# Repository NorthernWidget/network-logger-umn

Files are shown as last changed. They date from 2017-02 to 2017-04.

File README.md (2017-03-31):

Logger
======
This code is heavily based off the Alog library by Northern Widget. When
completed, this implementation will include radio telemetry using the RFM69 chip
for RF communication. This library is currently a work in progress and should
not be expected to work on its own. Expect a working copy in early May.
The new libraries in this repo are the Network.cpp, Network.h, Queue.cpp,
Queue.h, and Packet.h files. In total about 650 lines of code were added.

How to use the Network:

In order to use the network in the Logger Library, the user need only call 2
functions: sendOverNetwork(float data) with a floating point of the data that
they want to send to the coord, and then runNetwork(). runNetwork() is the
heart of the network library. It takes care of keeping up each nodes connection
to the coordinator, and handling any packets it receives or needs to send. A 
more detailed description of the algorithm can be found below, but these two
functions are all the end user NEEDS to get the network rolling.

A more detailed description:

The network algorithm works like so in pseudocode:

runNetwork()
{
	//condition 1 we are the coord listen for data
	if(IamCoord)
	{
		listen for incoming data and upload it to server
	}
	//condition 2 we have a connection to the coord, send data
	else if(IhaveConnectionToCoord)
	{
		send all of my data towards coord
		listen for data to forward to coord
	}
	//condition 3 we do not have connection to the coord
	else
	{
		try to connect to coordinator
	}
}
A few notable points in this algorithm. Originally, we were trying to forward
the data from the furthest leaf nodes to the router nodes first, then forward it
to the coordinator, but there is a nightmare of timing issues and other
complexities. Then we decided to do the opposite:send the data from the closest
nodes to the coordinator first. Therefore in condition 2, all the nodes that
aren't coord will be sending their data over and over again until it finally
reaches the coordinator. Then they will start listening for other nodes that
are using them as a next hop to get to the coord, and forward that data. This
eliminates a lot of the timing issues, and the need for each node to know the
other nodes depending on it.

Contributors to the network enabled ALog: Luke Cesarz, Jeff Worm, David Nickel,
Ying Yang, Bobby Schulz

Data logger library for the Arduino-based ALog (http://northernwidget.com/?page_id=8)

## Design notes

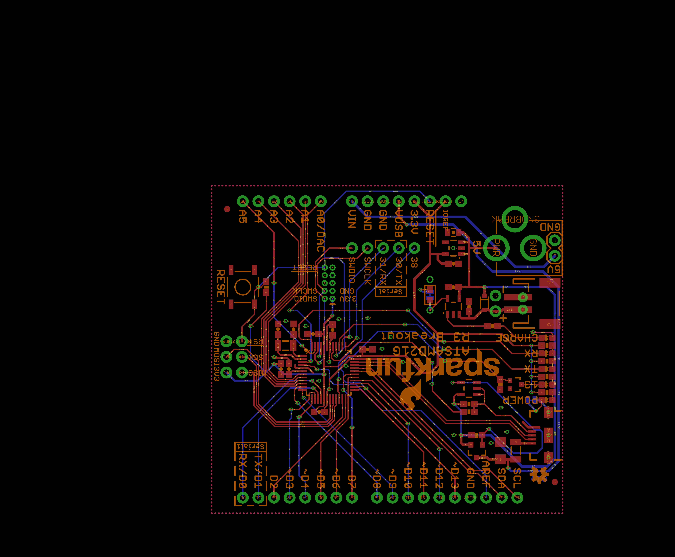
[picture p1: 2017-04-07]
Hardware/Logger v2/SAM21.png

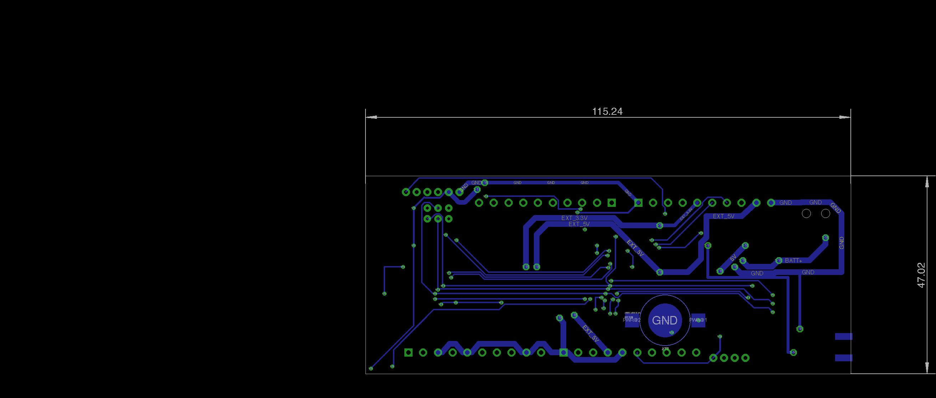
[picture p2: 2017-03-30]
Hardware/Logger v2/Logger_v2_BOTTOM.png

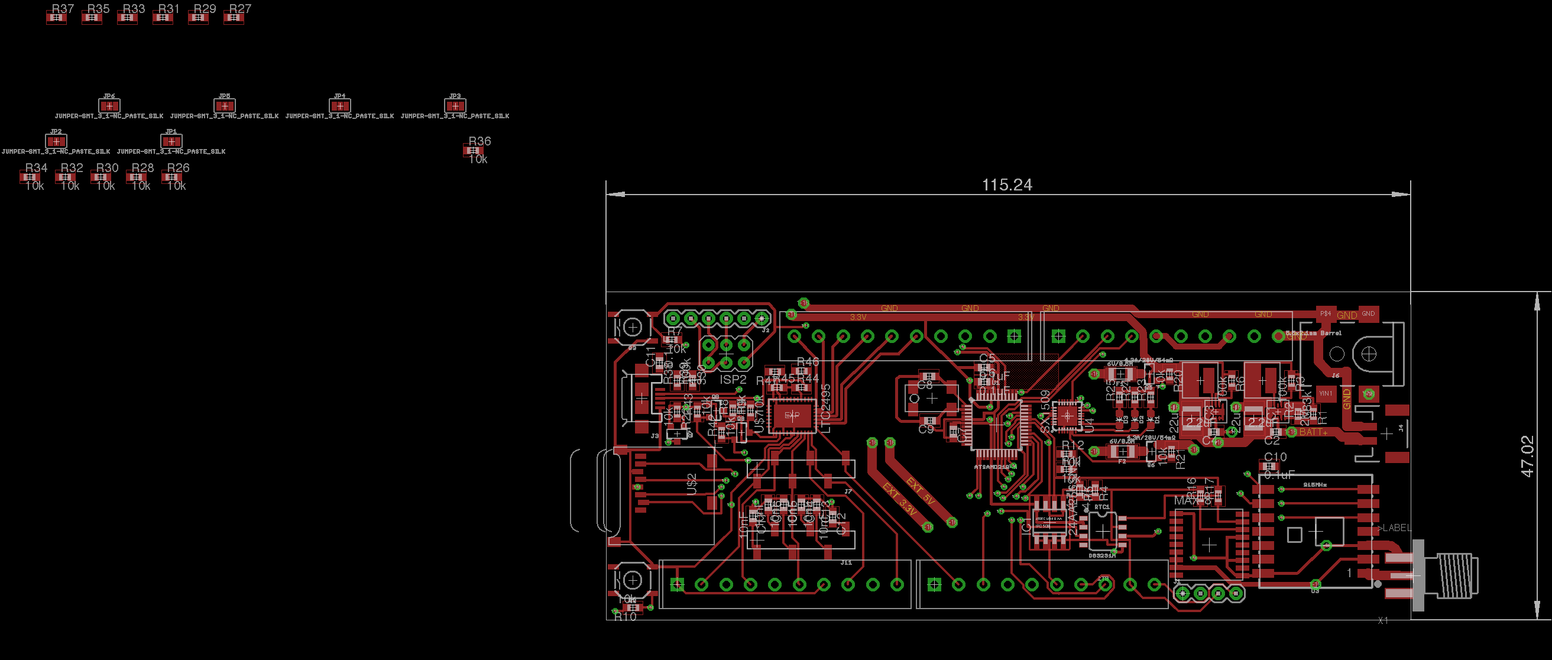
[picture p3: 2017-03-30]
Hardware/Logger v2/Logger_v2_TOP.png

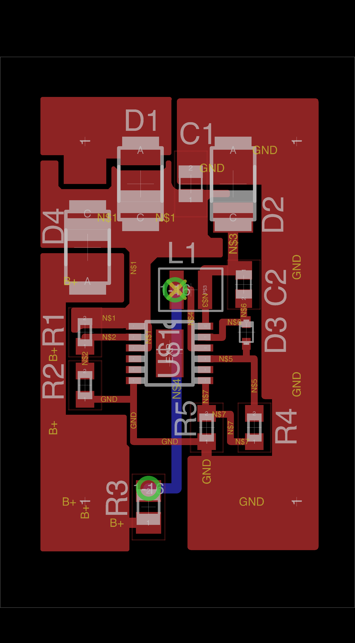
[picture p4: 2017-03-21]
Hardware/Senior Design Prototypes/Solar Charge Controller.png

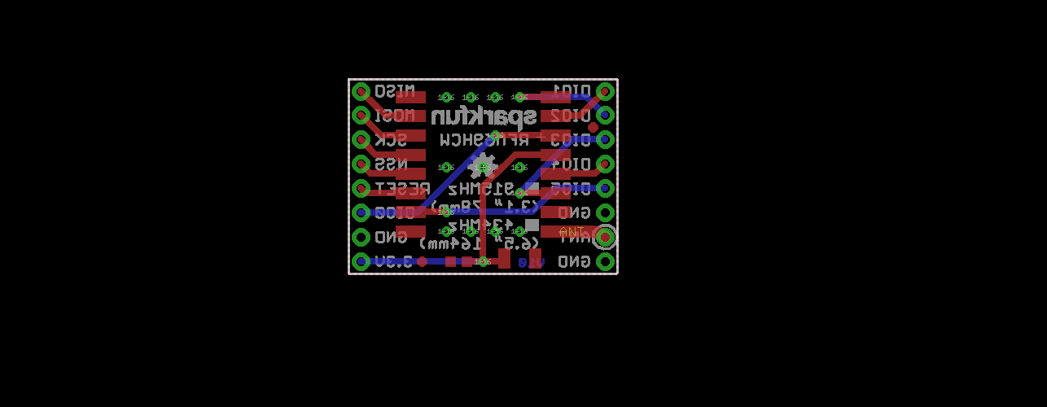
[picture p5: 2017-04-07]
Hardware/Logger v2/Radio.png

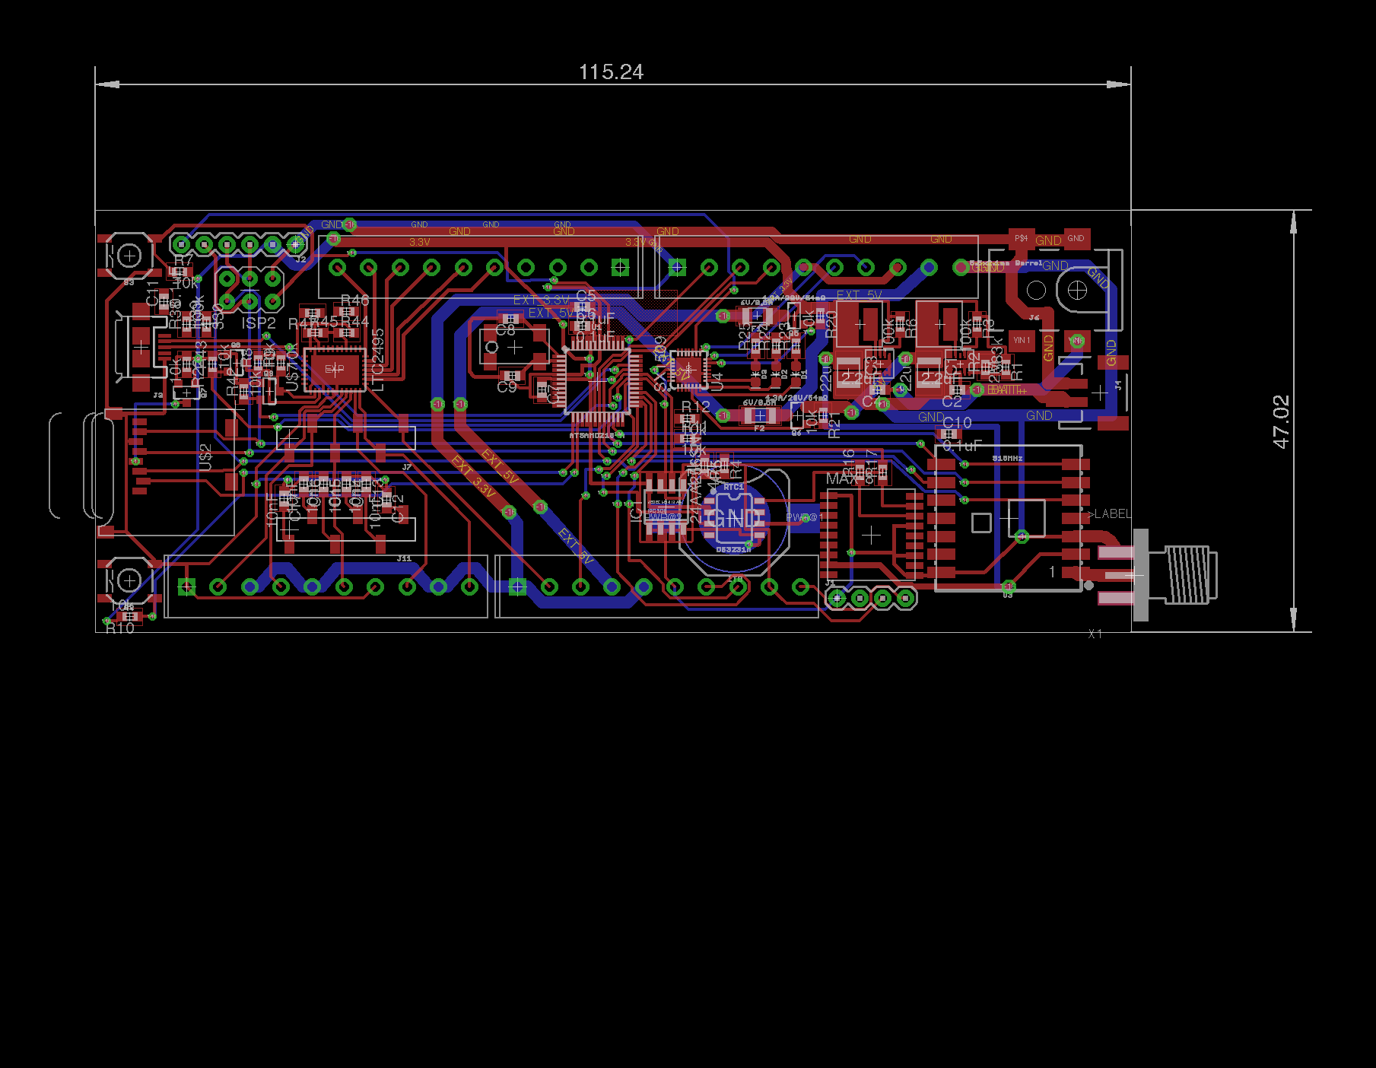
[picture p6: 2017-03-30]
Hardware/Logger v2/Logger_v2_FULL.png

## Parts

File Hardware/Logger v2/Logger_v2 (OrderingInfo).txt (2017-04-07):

Partlist exported from /Volumes/OSX_Storage/network-logger-umn/Hardware/Logger v2/Logger_v2.sch at 4/5/17 9:49 AM

Qty Value                    Device                     Package                Parts                                                                  Description                                                                                                     MF MPN           OC_FARNELL OC_NEWARK PROD_ID     SF_ID     VALUE           
1                            CONN_06SILK_FEMALE_PTH     1X06                   J2                                                                     Multi connection point. Often used as Generic Header-pin footprint for 0.1 inch spaced/style header connections                                       CONN-08437                            
2                            CONN_06SMD-STRAIGHT-FEMALE 1X06_SMD_STRAIGHT      J7, J11                                                                Multi connection point. Often used as Generic Header-pin footprint for 0.1 inch spaced/style header connections                                       CONN-10203                            
4                            CONN_10                    SCREWTERMINAL-3.5MM-10 J5, J8, J9, J10                                                        Multi connection point. Often used as Generic Header-pin footprint for 0.1 inch spaced/style header connections                                                                             
1                            I2C_STANDARD               1X04                   J1                                                                     SparkFun I2C Standard Pinout Header                                                                                                                                                         
1                            JST_2MM_MALE               JST-2-SMD              J4                                                                     JST 2MM MALE RA CONNECTOR                                                                                                                             CONN-11443  PRT-08612                 
3                            LED0603                    LED-0603               D1, D2, D3                                                             LED (Generic)                                                                                                                                                                               
1                            SMACONNECTOR_EDGE          SMA_EDGELAUNCH         X1                                                                     SMA Connector                                                                                                                                                                               
1                            USB_MICRO-B_SMT            USB-MICROB             J3                                                                     USB Type Micro-B Connector                                                                                                                            CONN-09505  PRT-08533                 
1   .1uF                     C-EUC0603                  C0603                  C18                                                                    CAPACITOR, European symbol                                                                                                                                                                  
4   0.1uF                    C-EUC0603                  C0603                  C5, C6, C10, C11                                                       CAPACITOR, European symbol                                                                                                                                                                  
3   100k                     R-EU_R0603                 R0603                  R3, R6, R38                                                            RESISTOR, European symbol                                                                                                                                                                   
15  10k                      R-EU_R0603                 R0603                  R7, R8, R9, R10, R11, R12, R20, R21, R22, R42, R43, R44, R45, R46, R47 RESISTOR, European symbol                                                                                                                                                                   
6   10nF                     C-EUC0603                  C0603                  C12, C13, C14, C15, C16, C17                                           CAPACITOR, European symbol                                                                                                                                                                  
2   10uH                     WE-LSQ(INDUCTOR)           WE-LQS(INDUCTOR)       L1, L2                                                                                                                                                                                                                                                             
2   12nF                     C-EUC0603                  C0603                  C8, C9                                                                 CAPACITOR, European symbol                                                                                                                                                                  
1   1uF                      C-EUC0603                  C0603                  C7                                                                     CAPACITOR, European symbol                                                                                                                                                                  
2   2.2uF                    C-EUC0603                  C0603                  C2, C4                                                                 CAPACITOR, European symbol                                                                                                                                                                  
2   220mA/50V/3.5Ω           MOSFET-NCH-BSS138          SOT23-3                Q8, Q9                                                                 N-channel MOSFETs                                                                                                                                     TRANS-00830           220mA/50V/3.5Ω  
2   22uF                     C-EUC1210                  C1210                  C1, C3                                                                 CAPACITOR, European symbol                                                                                                                                                                  
1   24AA256SN                24AA256SN                  SO-08                  IC1                                                                    Serial EEPROM                                                                                                      24AA256T-I/SM 1579570    08N6838                                         
1   2M                       R-EU_R0603                 R0603                  R1                                                                     RESISTOR, European symbol                                                                                                                                                                   
4   330                      R-EU_R0603                 R0603                  R23, R24, R25, R39                                                     RESISTOR, European symbol                                                                                                                                                                   
1   383k                     R-EU_R0603                 R0603                  R2                                                                     RESISTOR, European symbol                                                                                                                                                                   
3   4.3A/20V/54mΩ            MOSFET_PCH-IRLML2244       SOT23-3                Q5, Q6, Q7                                                             P-channel MOSFETs                                                                                                                                     TRANS-11153           4.3A/20V/54mΩ   
2   4.7k                     R-EU_R0603                 R0603                  R4, R5                                                                 RESISTOR, European symbol                                                                                                                                                                   
1   5.5x2.1mm Barrel         POWER_JACKSMD              POWER_JACK_SMD         J6                                                                     Power Jack Connector                                                                                                                                  CONN-08106  PRT-12748 5.5x2.1mm Barrel
2   6V/0.5A                  PPTC_HALF-AMP              1206                   F1, F2                                                                 Resettable Fuse PPTC                                                                                                                                  RES-08585             6V/0.5A         
1   915MHz                   RFM69HCW-915               RFM69HCW-XXXS2         U3                                                                     Hope RF RFM69H ISM Transceiver Module                                                                                                                 IC-11997              915MHz          
1   ATSAMD21G-A              ATSAMD21G-A                TQFP-48                U1                                                                     Atmel SAMD21G SMART ARM-Based Microcontroller                                                                                                         IC-13064                              
1   AVRISP-6                 AVRISP-6                   AVRISP                 ISP2                                                                   AVR ISP HEADER                                                                                                                                                                              
1   CM200                    CM200                      4-SOJ                  U$5                                                                    Crystal Oscilator, 32.768 kHz                                                                                                                                                               
1   DS3231M                  DS3231M                    SO08                   RTC1                                                                   DS3231M Real Time Clock                                                                                                                               IC-11985                              
4   FB                       R-EU_R0603                 R0603                  R13, R14, R16, R17                                                     RESISTOR, European symbol                                                                                                                                                                   
1   LINX-BAT-HLD-012-SMT-OTL LINX-BAT-HLD-012-SMT-OTL   LINX_BAT-HLD-012-SMT   BT1                                                                                                                                                                                                                                                                
1   LTC2495                  LTC2495                    QFN38-5X7              U$7                                                                                                                                                                                                                                                                
1   MICROSD                  MICROSD                    MICROSD                U$2                                                                    Micro-SD / Transflash card holder with SPI pinout                                                                                                                                           
2   SKRPABE010               SKRPABE010                 SKRPABE010_(SWITCH)    S2, U$1                                                                SPST Switch                                                                                                                                                                                 
1   SX1509                   SX1509                     QFN-28                 U4                                                                     Semtech SX1509                                                                                                                                        IC-11311              SX1509          
2   TPS6217X                 TPS6217X                   WSON-10                U$3, U$4                                                                                                                                                                                                                                                           
1   UBLOX_MAX-8              UBLOX_MAX-8                MAX-8                  U$6                                                                    UBLOX MAX-8 GPS module

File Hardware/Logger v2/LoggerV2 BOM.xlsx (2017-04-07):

Part Type | Part Name | Value | Digikey # | Notes | Quantity
IC | SAM21 | N/A | ATSAMD21G18A-AUTCT-ND (http://www.digikey.com/scripts/DkSearch/dksus.dll?Detail&itemSeq=224549847&uq=636269798465339910) | Microcontroller
IC | SX1509 |  | SX1509BIULCT-ND (http://www.digikey.com/scripts/DkSearch/dksus.dll?Detail&itemSeq=224323385&uq=636269798465339910) | IO Expander
IC | TPS62175 |  | 296-39451-1-ND (http://www.digikey.com/scripts/DkSearch/dksus.dll?Detail&itemSeq=221261223&uq=636269798465183897) | 5v regulator
IC | TPS62177 |  | 296-35097-1-ND (http://www.digikey.com/scripts/DkSearch/dksus.dll?Detail&itemSeq=221261202&uq=636269798465183897) | 3.3v regulator
Unit | RFM69HCW |  | 1568-1394-ND (http://www.digikey.com/scripts/DkSearch/dksus.dll?Detail&itemSeq=224552594&uq=636269815003341962) | 915MHz Radio
IC | 24AA256SN |  | 24AA256-I/SN-ND (http://www.digikey.com/scripts/DkSearch/dksus.dll?Detail&itemSeq=224320305&uq=636269798465339910) | EEPROM
IC | DS3231M |  | DS3231MZ/V+-ND (http://www.digikey.com/scripts/DkSearch/dksus.dll?Detail&itemSeq=224550127&uq=636269800175242390) | RTC
IC | LTC2495 |  | LTC2495IUHF#PBF-ND (http://www.digikey.com/scripts/DkSearch/dksus.dll?Detail&itemSeq=224317796&uq=636269800175242390) | ADC
Unit | UBLOX MAX-8 |  |  | GPS unit
Con | ISCP Header |  | 609-3234-ND (http://www.digikey.com/scripts/DkSearch/dksus.dll?Detail&itemSeq=224552432&uq=636269814345166360)
Con | Screw Terminal |  | ED2746-ND (http://www.digikey.com/scripts/DkSearch/dksus.dll?Detail&itemSeq=224553190&uq=636269819913539111) |  | 4
Con | JST Connector |  | 455-1749-1-ND (http://www.digikey.com/scripts/DkSearch/dksus.dll?Detail&itemSeq=224553041&uq=636269818815814360) | Battery connector
Con | Barrel Connector |  | 732-5929-1-ND (http://www.digikey.com/scripts/DkSearch/dksus.dll?Detail&itemSeq=224551901&uq=636269811824109048) | Vin/Battery connector (Verify connector)
Con | SMA Connector |  | CON-SMA-EDGE-S-ND (http://www.digikey.com/scripts/DkSearch/dksus.dll?Detail&itemSeq=224322970&uq=636269800175242390) | RF connector for radio
Con | Resistor Header |  | S5637-ND (http://www.digikey.com/scripts/DkSearch/dksus.dll?Detail&itemSeq=224317728&uq=636269800175242390) | 6 pin header for voltage divide resistors
Con | SD Holder |  | 101-00660-68-6-1-ND (http://www.digikey.com/scripts/DkSearch/dksus.dll?Detail&itemSeq=224314344&uq=636269800175242390)
Con | Micro USB |  | 609-4613-1-ND (http://www.digikey.com/scripts/DkSearch/dksus.dll?Detail&itemSeq=221261181&uq=636269800175242390)
Other | Battery Clip |  | BAT-HLD-012-SMT-ND (http://www.digikey.com/scripts/DkSearch/dksus.dll?Detail&itemSeq=224550456&uq=636269802903285708) | 12mm battery holder
Other | Button |  | MOUSER |  | 2
Other | Fuse |  | MF-USMF010-2CT-ND (http://www.digikey.com/scripts/DkSearch/dksus.dll?Detail&itemSeq=224319648&uq=636269800175242390) | 300 mA PTC fuse | 2
Transistor | IRLML2244 |  | IRLML2244TRPBFCT-ND (http://www.digikey.com/scripts/DkSearch/dksus.dll?Detail&itemSeq=224319962&uq=636269800175242390) | P-FET | 3
Transistor | BSS138 |  | BSS138NH6433XTMA1CT-ND (http://www.digikey.com/scripts/DkSearch/dksus.dll?Detail&itemSeq=224318071&uq=636269800175242390) | N-FET | 2
Other | Ferite beads |  | 490-5223-1-ND (http://www.digikey.com/scripts/DkSearch/dksus.dll?Detail&itemSeq=221261186&uq=636269800175086377) | 603
Other | LEDs |  | 160-1446-1-ND (http://www.digikey.com/scripts/DkSearch/dksus.dll?Detail&itemSeq=224552249&uq=636269813361617163) | Color variable, 0603 (PN coresponds to Green) | 3
Other | 32kHz Crystal |  | 300-8742-1-ND (http://www.digikey.com/scripts/DkSearch/dksus.dll?Detail&itemSeq=221261176&uq=636269819913383098)
Passive | Inductor | 10uH | 732-5519-1-ND (http://www.digikey.com/scripts/DkSearch/dksus.dll?Detail&itemSeq=224325596&uq=636269819913539111) | For voltage regulators | 2
Passive | Capacitor | 0.1uF |  |  | 5
Passive | Capacitor | 1uF |  |  | 1
Passive | Capacitor | 2.2uF |  |  | 2
Passive | Capacitor | 22uF |  |  | 2
Passive | Capacitor | 10nF |  |  | 6
Passive | Capacitor | 12nF |  |  | 2
Passive | Resistor | 100k |  |  | 3
Passive | Resistor | 10k |  |  | 15
Passive | Resistor | 2M |  |  | 1
Passive | Resistor | 330 |  |  | 4
Passive | Resistor | 383k |  |  | 1
Passive | Resistor | 4.7k |  |  | 2

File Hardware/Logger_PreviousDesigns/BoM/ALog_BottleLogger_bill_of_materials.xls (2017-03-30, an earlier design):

Manufacturer | Manufacturer Part Number | Part Description | Device Usage | Quantity
KEMET (VA) | C0603C105K8PACTU | CAP CER 1UF 10V X5R 0603 | DECOUPLING VCC and VCC/CLOCK BATT, RESET | 5
YAGEO (VA) | RC0603JR-07220RL | RES SMD 220 OHM 5% 1/10W 0603 | LED; CLOCK BACKUP BATTERY POWER SWITCHING | 3
ON SHORE TECHNOLOGY INC | OSTTE100104 | TERMINAL BLOCK 3.5MM 10POS PCB | SCREW TERMINAL - 10 | 3
TDK CORPORATION (VA) | CKCA43X7R1H103M100AA | CAP ARRAY 10000PF 50V X7R 1206 | ADC, SD/RTC, AND VCC DECOUPLING | 2
KEMET (VA) | C0603C330J5GACTU | CAP CER 33PF 50V NP0 0603 | XTAL CAPS | 2
Samtec | SSW-106-22-S-S | CONN HEADER FEMALE 6POS .1" GOLD | REFERENCE RESISTORS - 6 PIN | 2
NXP SEMICONDUCTORS (VA) | 2N7002PW,115 | MOSFET N-CH 60V 0.31A SOT323 | I2C LEVEL SHIFT | 2
FAIRCHILD SEMICONDUCTOR (VA) | FDN360P | MOSFET P-CH 30V 2A SSOT3 | HELP IN AUTOMATIC POWER SUPPLY SWITCHING | 2
YAGEO (VA) | RC0603JR-0727RL | RES SMD 27 OHM 5% 1/10W 0603 | USB DATA I/O | 2
Texas Instruments | TPS60150DRVR | IC REG SWTCHD CAP 5V 0.14A 6SON | 5V charge pump, 5.17 until about 10ma | 1
AMPHENOL FCI | 69192-406 | CONN HEADER VERT DUAL 6POS | AVRISP MKII | 1
TE CONNECTIVITY AMP (VA) | 2041021-4 | CONN SD CARD PUSH-PULL R/A SMD | SD CARD HOLDER | 1
CTS-FREQUENCY CONTROLS | ATS08A-E | CRYSTAL 8.0000MHZ 20PF T/H | MCU OSCILLATOR | 1
Bourns Inc. | CV201210-100K | FIXED IND 10UH 150MA 360 MOHM | LOW PASS FILTER TO ADC | 1
TEXAS INSTRUMENTS (VA) | CD74HC4050M96 | IC BUFFER HEX 1INPUT 16SOIC | 4050 LEVEL SHIFTER: SD | 1
LINEAR TECHNOLOGY (VA) | LTC4412ES6#TRMPBF | IC OR CTRLR SRC SELECT TSOT23-6 | AUTOMATIC POWER SUPPLY SWITCHING - MAIN CHIP | 1
LITE-ON INC (VA) | LTST-C190KSKT | LED YELLOW CLEAR 0603 SMD | RX LED | 1
CTS Resistor Products | 742C083102JP | RES ARRAY 4 RES 1K OHM 1206 | RES ARRAY 4 RES 1K OHM 603 | 1
CTS Resistor Products | 742C083332JP | RES ARRAY 4 RES 3.3K OHM 1206 | RES ARRAY 4 RES 3.3K OHM 603 | 1
STACKPOLE ELECTRONICS INC (VA) | RMCF0603FT470K | RES SMD 470K OHM 1% 1/10W 0603 | POWER SUPPLY SWITCHING | 1
AMPHENOL FCI | 61729-1011BLF | USB RCPT B-TYPE R/A FULL BACK | USB PLUG | 1
Microchip Technology | MIC5380-SSYFT-TR | IC REG LDO 3.3V 0.15A 6TMLF | Linear Voltage Regulator Fixed 2 Output 3.3V 150mA | 1
KEMET (VA) | C0603C104K4RACTU | CAP CER 0.1UF 16V X7R 0603 | DECOUPLING (FTDI VCCIO, 328P VCC) | 5
YAGEO (VA) | CC0603KRX5R6BB225 | CAP CER 2.2UF 10V X5R 0603 | LDO REGULATOR & VCC DECOUPLING | 3
TAIYO YUDEN (VA) | LMK316BJ106KL-T | CAP CER 10UF 10V X5R 1206 | USB DECOUPLING, AND BOOST CONVERTER | 2
TE CONNECTIVITY ALCOSWITCH | 1825910-6 | SWITCH TACTILE SPST-NO 0.05A 24V | RESET & LOG BUTTONS | 2
ENERGIZER BATTERY COMPANY | CR1220VP | BATTERY LITHIUM 3V COIN 12.5MM | COIN CELL: CLOCK BACKUP BATTERY | 1
Samsung Electro-Mechanics America, Inc. Samsung Electro-Mechanics America, Inc. | CL10A475MP5LNNC | CAP CER 4.7UF 10V X5R 0603 | CHARGE PUMP CAPACITOR | 1
CUI INC | PJ-202A | CONN POWER JACK 2.1MM PCB | POWER PLUG | 1
ATMEL | ATMEGA328P-MN | IC MCU 8BIT 32KB FLASH 32VQFN | MICROCONTROLLER CORE | 1
MAXIM INTEGRATED | DS3231MZ/V+ | IC RTC CLK/CALENDAR I2C 8-SOIC | REAL TIME CLOCK (RTC) | 1
FTDI | FT231XQ-T | IC USB SERIAL FULL UART 20QFN | FTDI USB | 1
Linear Technology | LT1461CIS8-3.3#PBF | IC VREF SERIES 3.3V 8SOIC | PRECISION 3.3V 100MA 0.08%, 12PPM/C | 1
KINGBRIGHT COMPANY LLC (VA) | APT1608QBC/D | LED BLUE CLEAR 0603 SMD | TX LED | 1
KINGBRIGHT COMPANY LLC | WP710A10SRD/D | LED RED DIFF 3MM ROUND T/H | FLASHING MESSAGES: INDICATOR LED | 1
STACKPOLE ELECTRONICS INC (VA) | RMCF0603JT10K0 | RES SMD 10K OHM 5% 1/10W 0603 | PULL UP FOR RESET | 1
KEYSTONE ELECTRONICS | 3001 | HOLDER BATTERY COIN 12MM DIA THM | CLOCK BACKUP BATTERY HOLDER | 1
DIODES INCORPORATED | BAT54C-7-F | DIODE ARRAY SCHOTTKY 30V SOT23-3 | DIODE ARRAY FOR BATT VS REGULATOR CLOCK POWER | 2
TDK CORPORATION (VA) | C1608NP01H470J080AA | CAP CER 47PF 50V NP0 0603 | USB-SERIAL | 0
Murata Electronics North America | LQH32PN4R7NN0L | ED IND 4.7UH 1A 180 MOHM SMD | 4.7UH INDUCTOR FOR BOOST CONVERTER | 0
Texas Instruments | TPS61222DCKR | IC REG BOOST 5V 0.2A SYNC SC70-6 | 3.3 TO 5V BOOST CONVERTER | 0
TEXAS INSTRUMENTS (VA) | MIC5305-3.3YD5-TR | IC REG LDO 3.3V 0.15A SOT23-5 | Linear Voltage Regulator IC Positive Fixed Output 3.3V 150mA | 0
STACKPOLE ELECTRONICS INC (VA) | RMCF0603FT1K00 | RES SMD 1K OHM 1% 1/10W 0603 | RX/TX RESISTORS | 0
YAGEO (VA) | RC0603JR-073KL | RES SMD 3K OHM 5% 1/10W 0603 | RTC PULL-UPS | 0
C&K COMPONENTS | PVA1 OA H4 1.2N V2 | SWITCH PUSH DPST-NO 0.1A 32V | MANUAL LOG BUTTON ("LOG NOW") | 0
Torex Semiconductor Ltd | XC9140A501MR-G | IC REG BST 5V 295MA SYNC SOT-25 | 3.3 TO 5V BOOST CONVERTER | 0
ON SHORE TECHNOLOGY INC | OSTTE040104 | TERMINAL BLOCK 3.5MM 4POS PCB | SCREW TERMINAL - 4 | 0
ON SHORE TECHNOLOGY INC | OSTTE080104 | TERMINAL BLOCK 3.5MM 8POS PCB | SCREW TERMINAL - 8 | 0
JST Sales America Inc. | B2B-XH-A(LF)(SN) |  | 2 Positions Header, Shrouded Connector 0.098" (2.50mm) Through Hole Tin | 1

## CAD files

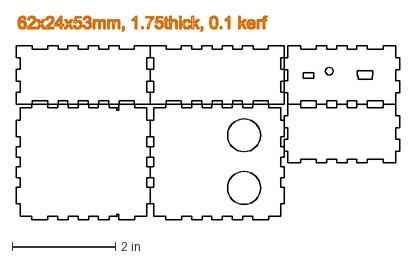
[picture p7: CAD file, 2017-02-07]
RFM69/examples/LowPowerLab_examples/SonarMote/SonarMote_lasercut plans_1.75mm acrylic.dxf
7.41 x 3.94 in

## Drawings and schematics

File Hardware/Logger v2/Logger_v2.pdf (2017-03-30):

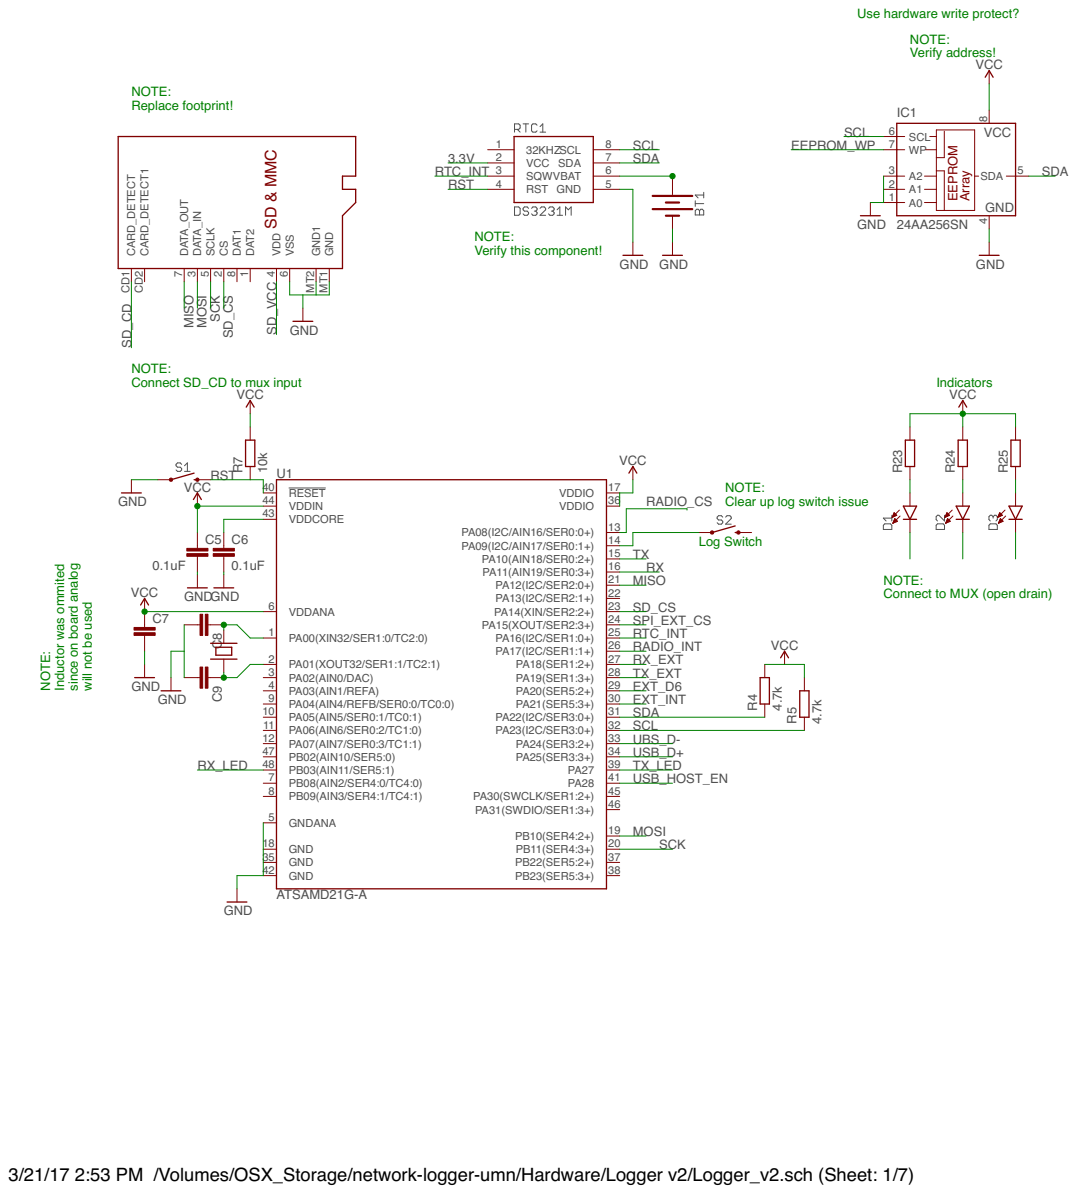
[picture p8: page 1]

Use hardware write protect?

NOTE: Verify this component!

NOTE: Connect SD_CD to mux input

NOTE: Clear up log switch issue

since on board analog will not be used

NOTE: Connect to MUX (open drain)

3/21/17 2:53 PM /Volumes/OSX_Storage/network-logger-umn/Hardware/Logger v2/Logger_v2.sch (Sheet: 1/7)

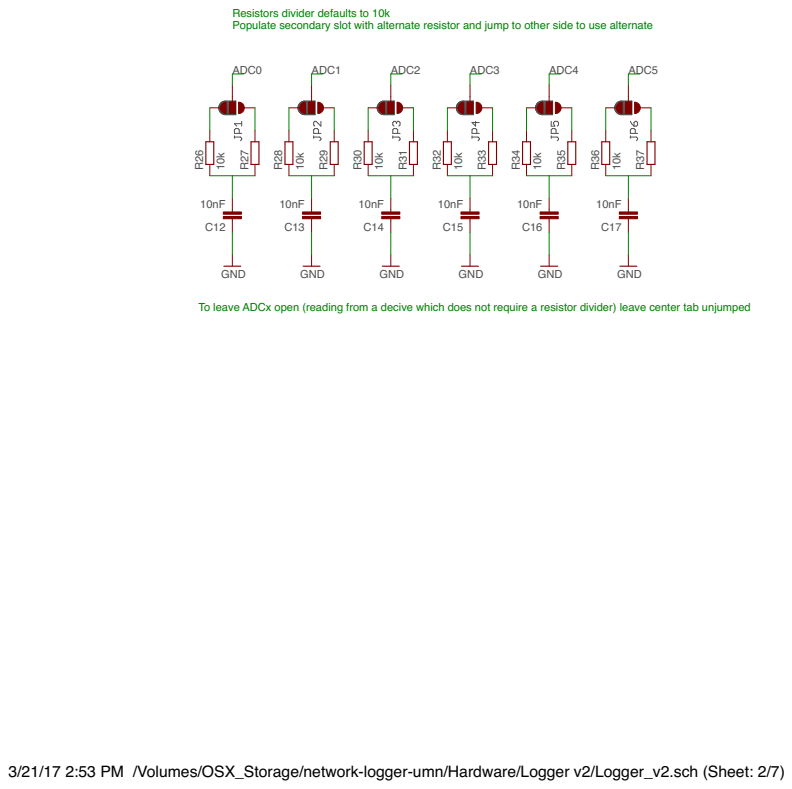
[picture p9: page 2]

Resistors divider defaults to 10k
Populate secondary slot with alternate resistor and jump to other side to use alternate

To leave ADCx open (reading from a decive which does not require a resistor divider) leave center tab unjumped

3/21/17 2:53 PM /Volumes/OSX_Storage/network-logger-umn/Hardware/Logger v2/Logger_v2.sch (Sheet: 2/7)

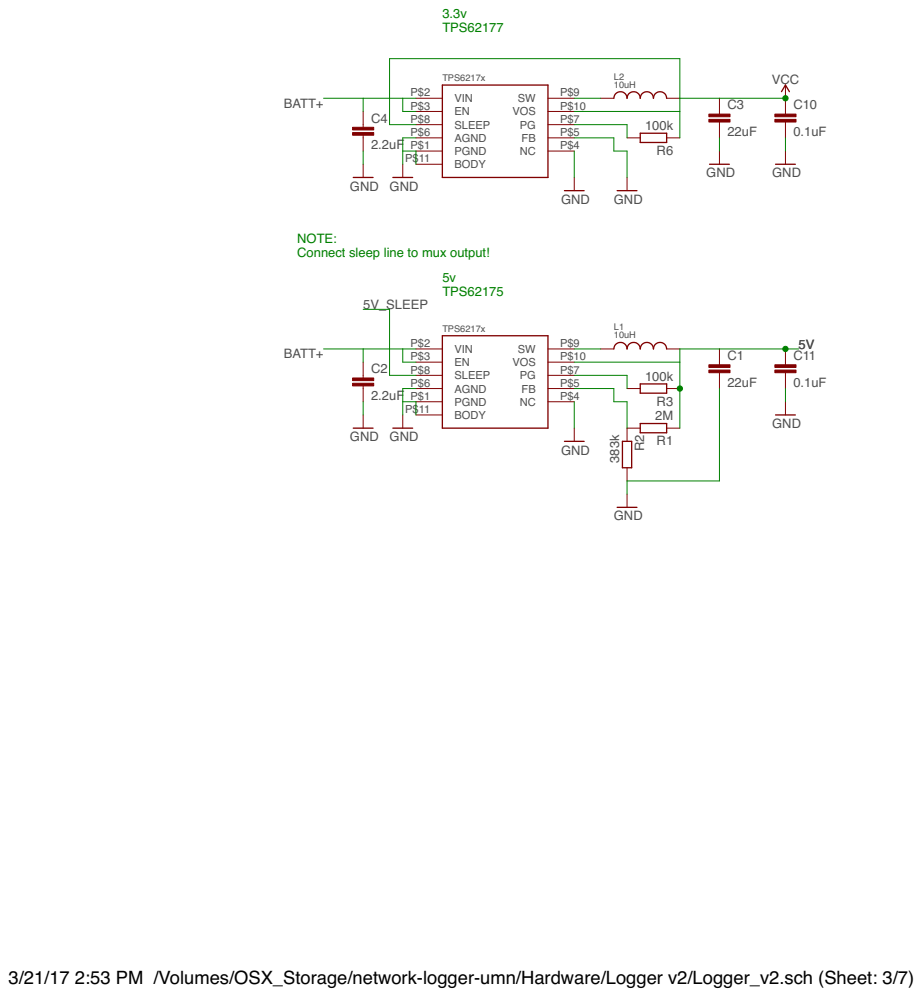
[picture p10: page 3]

NOTE: Connect sleep line to mux output!

3/21/17 2:53 PM /Volumes/OSX_Storage/network-logger-umn/Hardware/Logger v2/Logger_v2.sch (Sheet: 3/7)

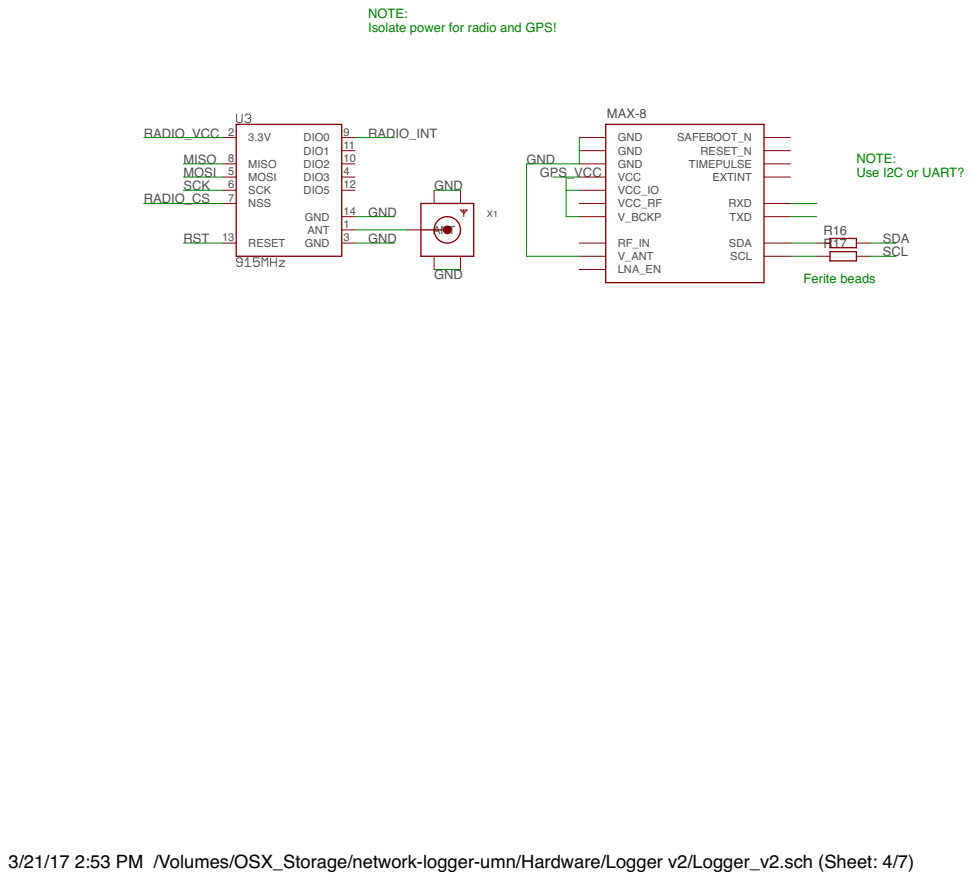
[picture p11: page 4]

NOTE:
Isolate power for radio and GPS!

NOTE: Use I2C or UART?

3/21/17 2:53 PM /Volumes/OSX_Storage/network-logger-umn/Hardware/Logger v2/Logger_v2.sch (Sheet: 4/7)

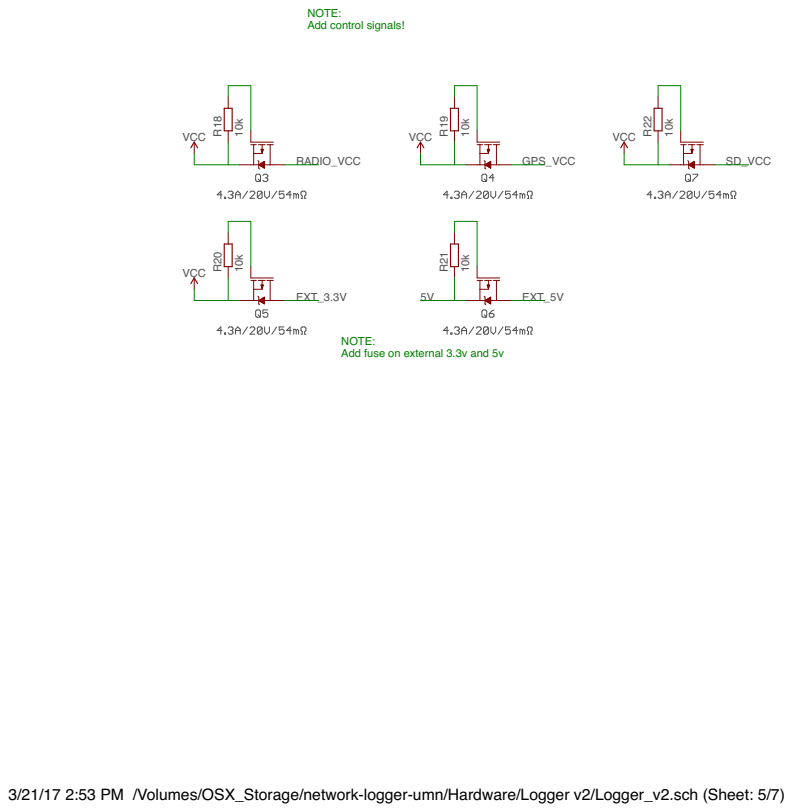
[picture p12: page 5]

NOTE: Add control signals!

NOTE: Add fuse on external 3.3v and 5v

3/21/17 2:53 PM /Volumes/OSX_Storage/network-logger-umn/Hardware/Logger v2/Logger_v2.sch (Sheet: 5/7)

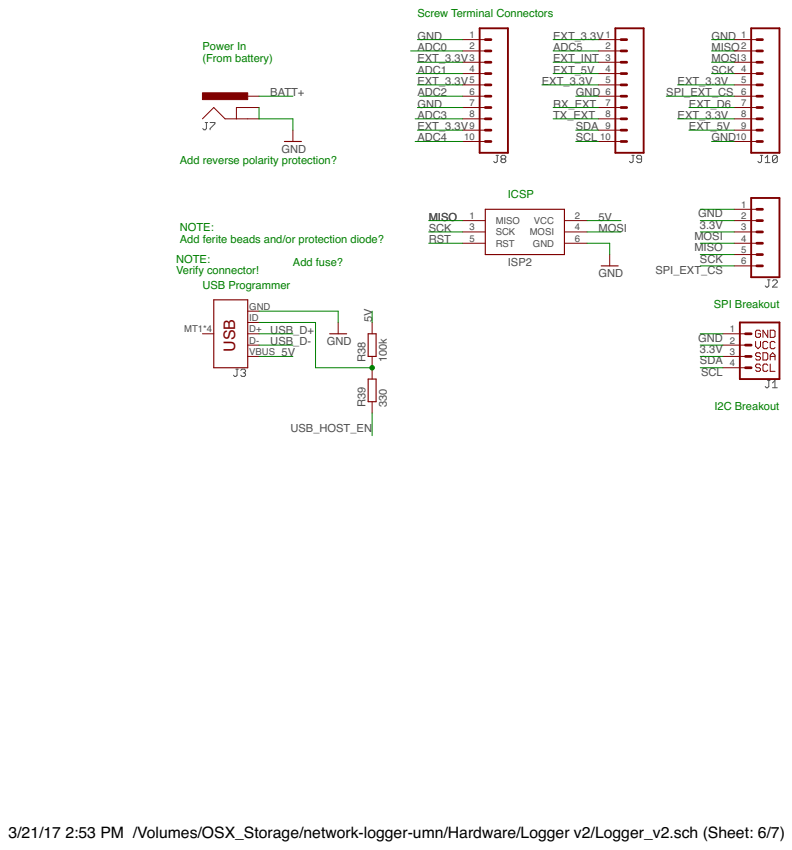
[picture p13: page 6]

Add reverse polarity protection?

NOTE: Add ferite beads and/or protection diode?

3/21/17 2:53 PM /Volumes/OSX_Storage/network-logger-umn/Hardware/Logger v2/Logger_v2.sch (Sheet: 6/7)

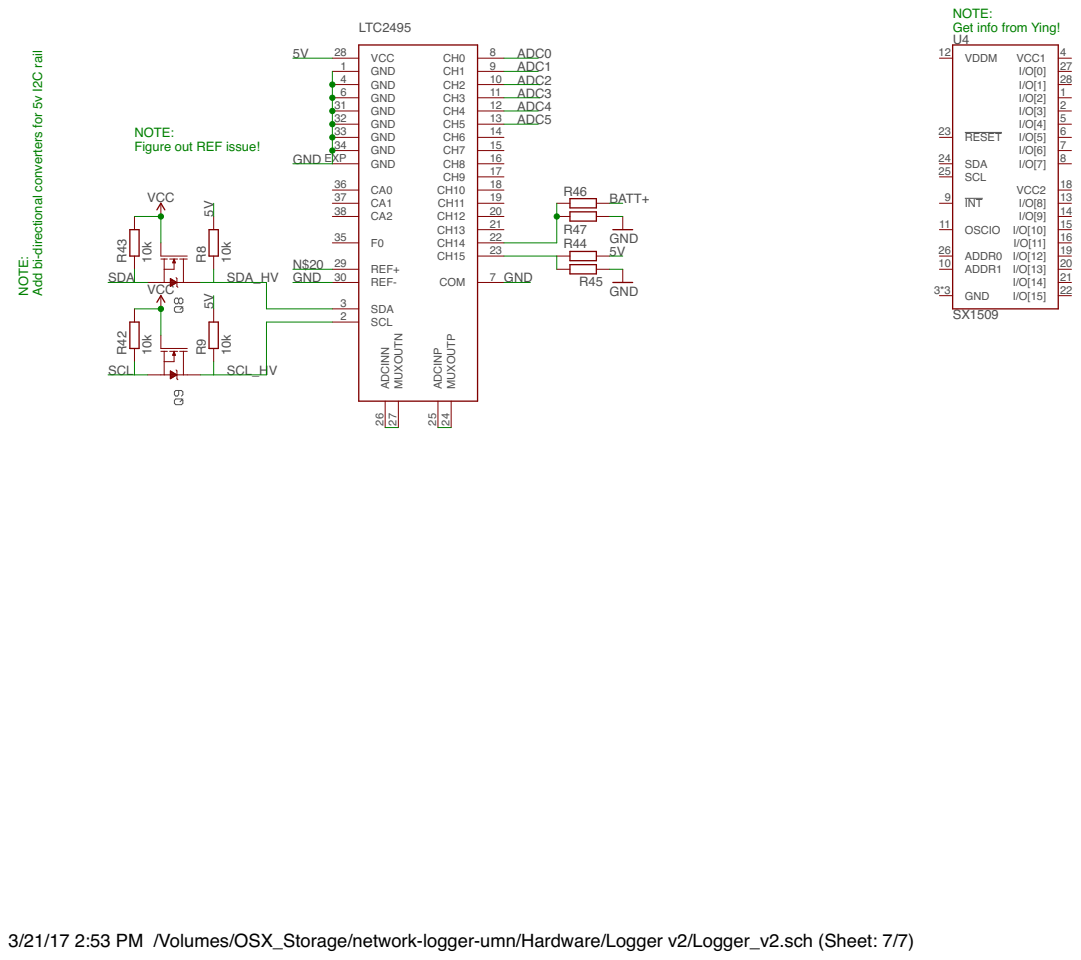
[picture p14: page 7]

NOTE: Get info from Ying!

3/21/17 2:53 PM /Volumes/OSX_Storage/network-logger-umn/Hardware/Logger v2/Logger_v2.sch (Sheet: 7/7)

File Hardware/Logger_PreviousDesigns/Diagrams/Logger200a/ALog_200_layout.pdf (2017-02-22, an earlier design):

# ALog BottleLogger v2.0.0

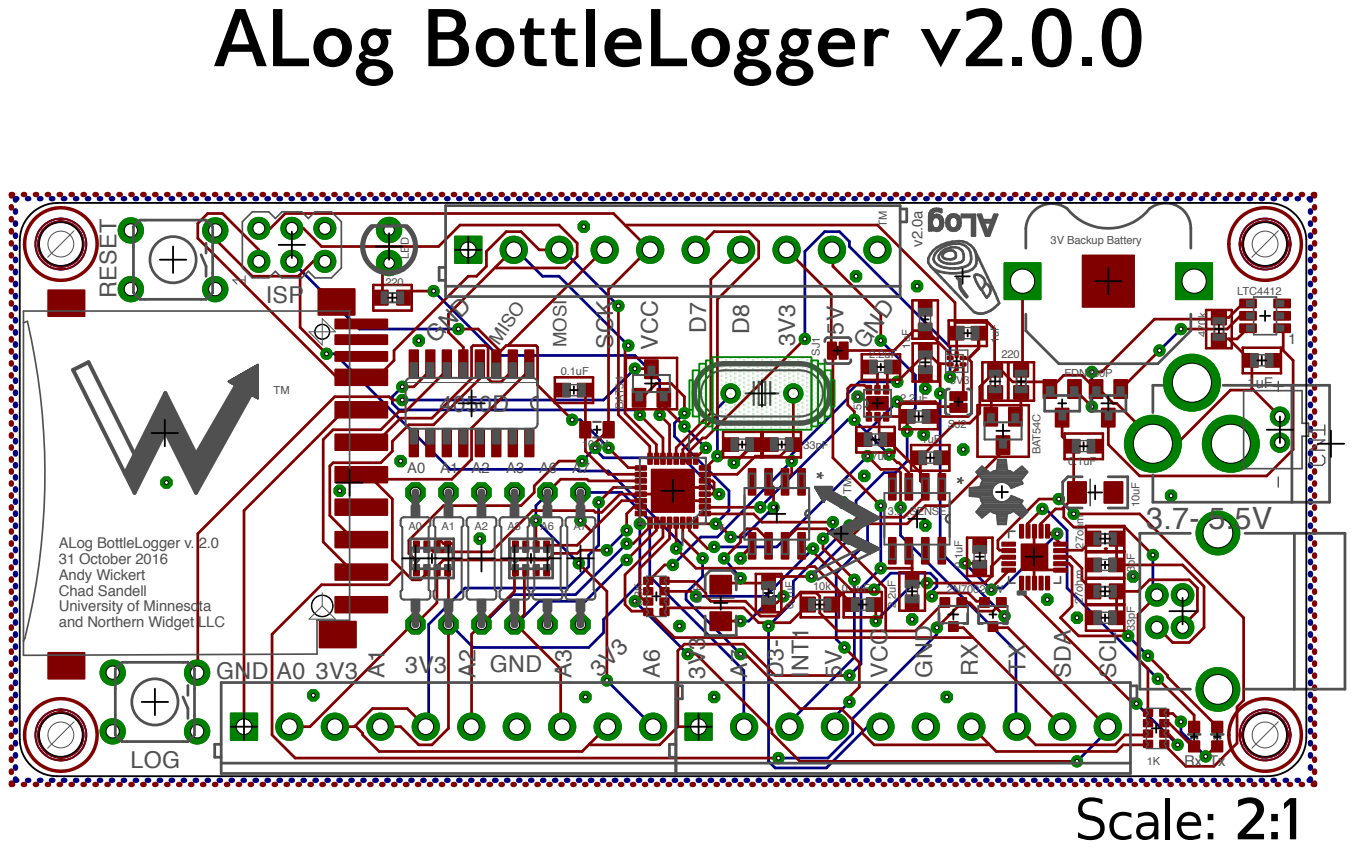
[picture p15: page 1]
GND; INT1; VCC; MOSI; SCK; SDA; SCL; MISO; ISP; LED; RESET; LOG; 3.3_SENSE; 3V Backup Battery; FDN360P; LTC4412; BAT54C; BAT54; 27ohm 27ohm; Scale: 2:1

ALog BottleLogger v. 2.0
31 October 2016
Andy Wickert
Chad Sandell
University of Minnesota
and Northern Widget LLC

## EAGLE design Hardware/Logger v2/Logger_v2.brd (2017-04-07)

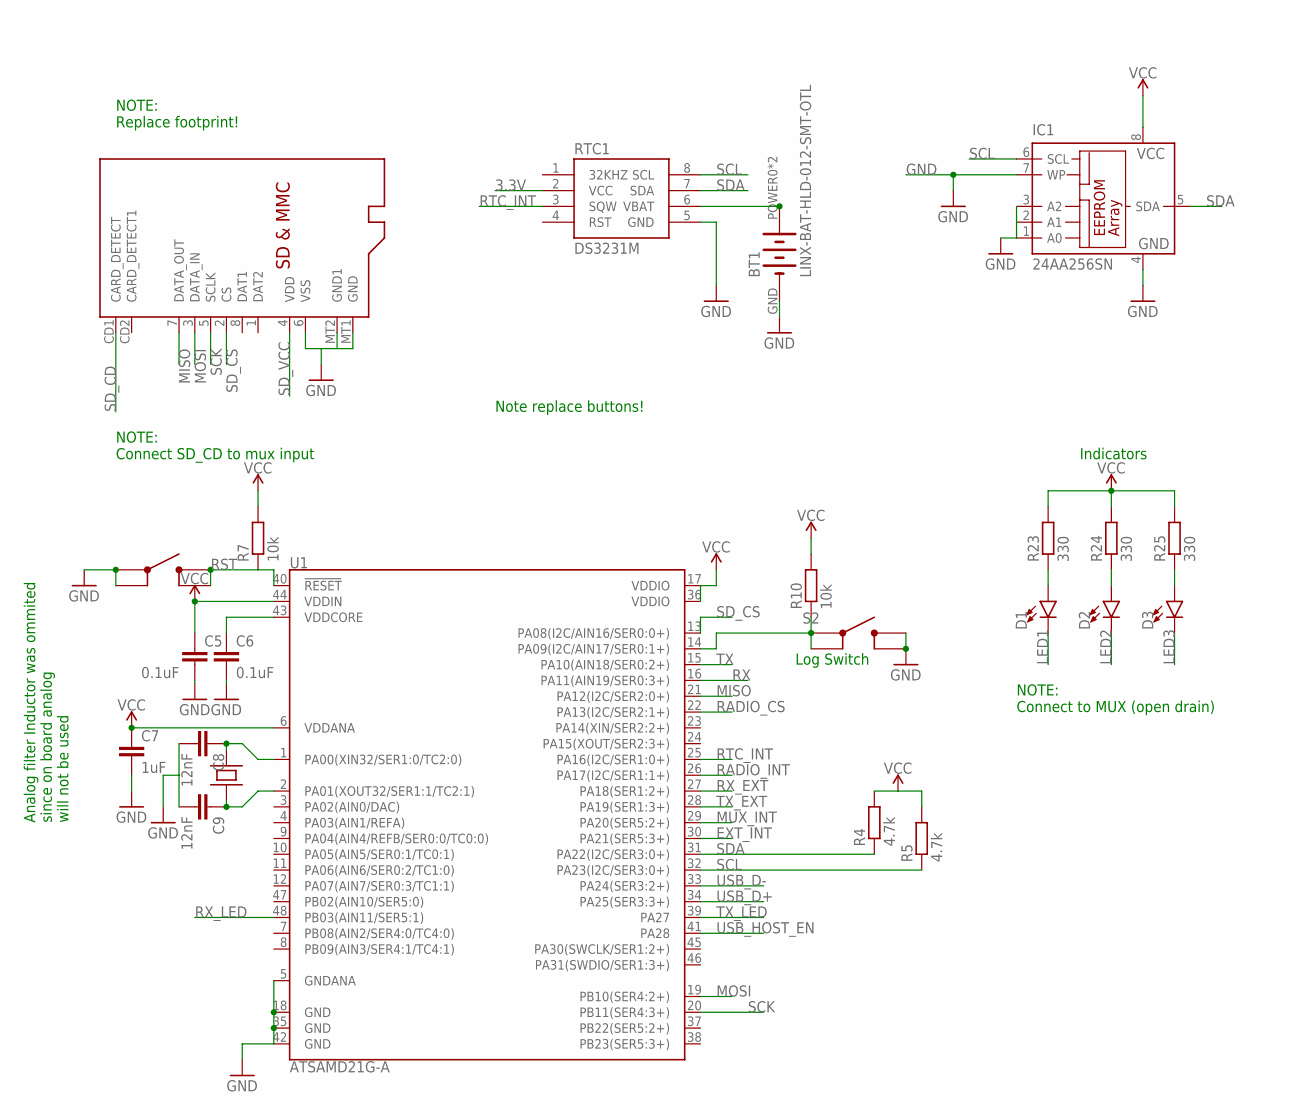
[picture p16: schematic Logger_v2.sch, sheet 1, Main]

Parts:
BT1: LINX-BAT-HLD-012-SMT-OTL; LINX_BAT-HLD-012-SMT
C5, C6: 0.1uF; C0603
C7: 1uF; C0603
C8, C9: 12nF; C0603
D1, D2, D3: LED0603; LED-0603
IC1: 24AA256SN; SO-08
R4, R5: 4.7k; R0603
R7, R10: 10k; R0603
R23, R24, R25: 330; R0603
RTC1: DS3231M; SO08
S2: SKRPABE010; SKRPABE010_(SWITCH)
U1: ATSAMD21G-A; TQFP-48
U$1: SKRPABE010; SKRPABE010_(SWITCH)
U$2: MICROSD
U$5: CM200; 4-SOJ

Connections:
3.3V: C5.1, C7.1, IC1.8 (VCC), R4.2, R5.2, R7.2, R10.2, R23.2, R24.2, R25.2, RTC1.2 (VCC), U1.6 (VDDANA), U1.17 (VDDIO), U1.36 (VDDIO), U1.44 (VDDIN); also elsewhere on the board
EXT_INT: U1.30 (PA21(SER5:3+)); also elsewhere on the board
GND: BT1.GND (-), C5.2, C6.2, C7.2, C8.2, C9.2, IC1.1 (A0), IC1.2 (A1), IC1.3 (A2), IC1.4 (GND), IC1.7 (WP), RTC1.5 (GND), S2.P$3 (3), S2.P$4 (4), U1.5 (GNDANA), U1.18 (GND), U1.35 (GND), U1.42 (GND), U$1.P$1 (1), U$1.P$2 (2), U$2.6 (VSS), U$2.MT1 (GND), U$2.MT2 (GND1); also elsewhere on the board
LED1: D1.C; also elsewhere on the board
LED2: D2.C; also elsewhere on the board
LED3: D3.C; also elsewhere on the board
MISO: U1.21 (PA12(I2C/SER2:0+)), U$2.7 (DATA_OUT); also elsewhere on the board
MOSI: U1.19 (PB10(SER4:2+)), U$2.3 (DATA_IN); also elsewhere on the board
MUX_INT: U1.29 (PA20(SER5:2+)); also elsewhere on the board
unnamed: R10.1, S2.P$1 (1), S2.P$2 (2), U1.14 (PA09(I2C/AIN17/SER0:1+))
unnamed: C6.1, U1.43 (VDDCORE)
unnamed: C8.1, U1.1 (PA00(XIN32/SER1:0/TC2:0)), U$5.P$4
unnamed: C9.1, U1.2 (PA01(XOUT32/SER1:1/TC2:1)), U$5.P$1
unnamed: BT1.POWER0 (+), BT1.POWER1 (+), RTC1.6 (VBAT)
unnamed: D1.A, R23.1
unnamed: D2.A, R24.1
unnamed: D3.A, R25.1
RADIO_CS: U1.22 (PA13(I2C/SER2:1+)); also elsewhere on the board
RADIO_INT: U1.26 (PA17(I2C/SER1:1+)); also elsewhere on the board
RST: R7.1, U1.40 (!RESET!), U$1.P$3 (3), U$1.P$4 (4); also elsewhere on the board
RTC_INT: RTC1.3 (SQW), U1.25 (PA16(I2C/SER1:0+))
RX: U1.16 (PA11(AIN19/SER0:3+))
RX_EXT: U1.27 (PA18(SER1:2+)); also elsewhere on the board
RX_LED: U1.48 (PB03(AIN11/SER5:1))
SCK: U1.20 (PB11(SER4:3+)), U$2.5 (SCLK); also elsewhere on the board
SCL: IC1.6 (SCL), R5.1, RTC1.8 (SCL), U1.32 (PA23(I2C/SER3:0+)); also elsewhere on the board
SDA: IC1.5 (SDA), R4.1, RTC1.7 (SDA), U1.31 (PA22(I2C/SER3:0+)); also elsewhere on the board
SD_CD: U$2.CD1 (CARD_DETECT)
SD_CS: U1.13 (PA08(I2C/AIN16/SER0:0+)), U$2.2 (CS)
SD_VCC: U$2.4 (VDD); also elsewhere on the board
TX: U1.15 (PA10(AIN18/SER0:2+))
TX_EXT: U1.28 (PA19(SER1:3+)); also elsewhere on the board
TX_LED: U1.39 (PA27)
USB_D+: U1.34 (PA25(SER3:3+)); also elsewhere on the board
USB_D-: U1.33 (PA24(SER3:2+)); also elsewhere on the board
USB_HOST_EN: U1.41 (PA28); also elsewhere on the board

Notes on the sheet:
NOTE: Replace footprint!
Log Switch
Analog filter Inductor was ommited since on board analog will not be used
Indicators
NOTE: Connect to MUX (open drain)
NOTE: Connect SD_CD to mux input
Note replace buttons!

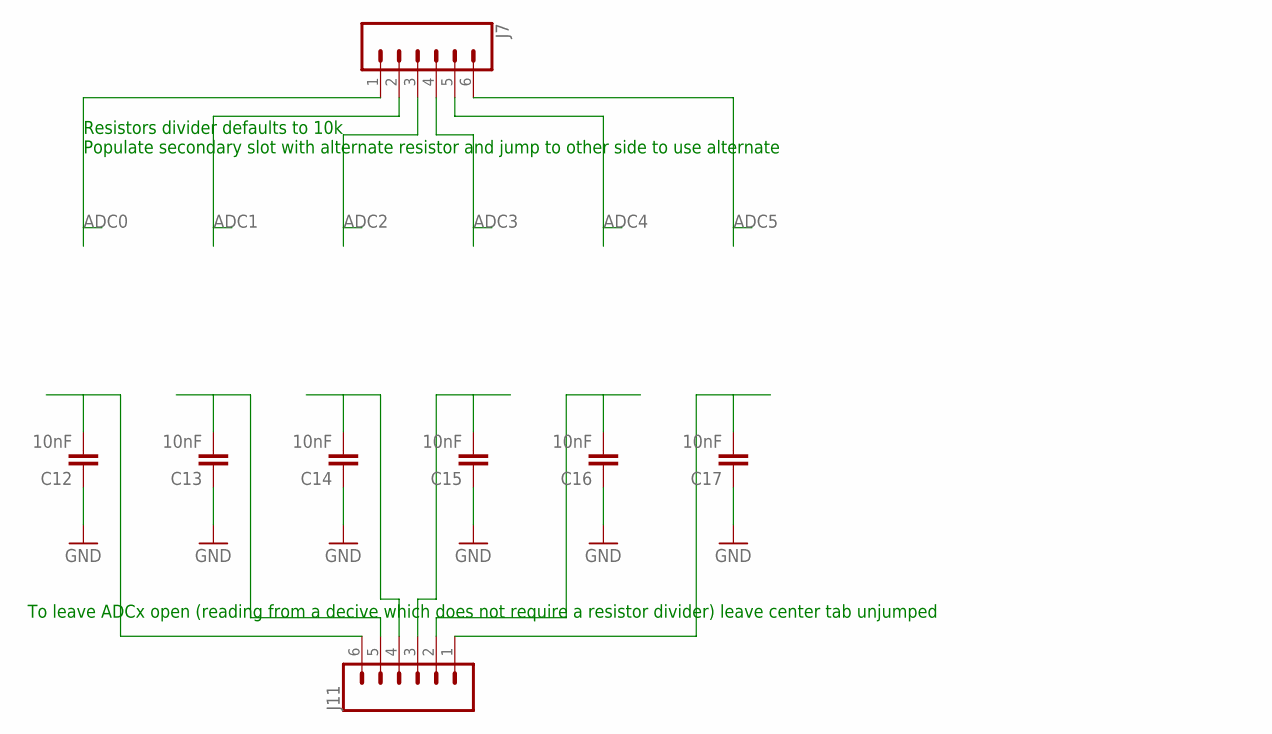
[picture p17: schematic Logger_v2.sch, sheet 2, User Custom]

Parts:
C12, C13, C14, C15, C16, C17: 10nF; C0603
J7, J11: CONN_06SMD-STRAIGHT-FEMALE; 1X06_SMD_STRAIGHT

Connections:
ADC0: J7.1; also elsewhere on the board
ADC1: J7.2; also elsewhere on the board
ADC2: J7.3; also elsewhere on the board
ADC3: J7.4; also elsewhere on the board
ADC4: J7.5; also elsewhere on the board
ADC5: J7.6; also elsewhere on the board
GND: C12.1, C13.1, C14.1, C15.1, C16.1, C17.1; also elsewhere on the board
unnamed: C12.2, J11.6
unnamed: C13.2, J11.5
unnamed: C14.2, J11.4
unnamed: C15.2, J11.3
unnamed: C16.2, J11.2
unnamed: C17.2, J11.1

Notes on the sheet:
Resistors divider defaults to 10k Populate secondary slot with alternate resistor and jump to other side to use alternate
To leave ADCx open (reading from a decive which does not require a resistor divider) leave center tab unjumped

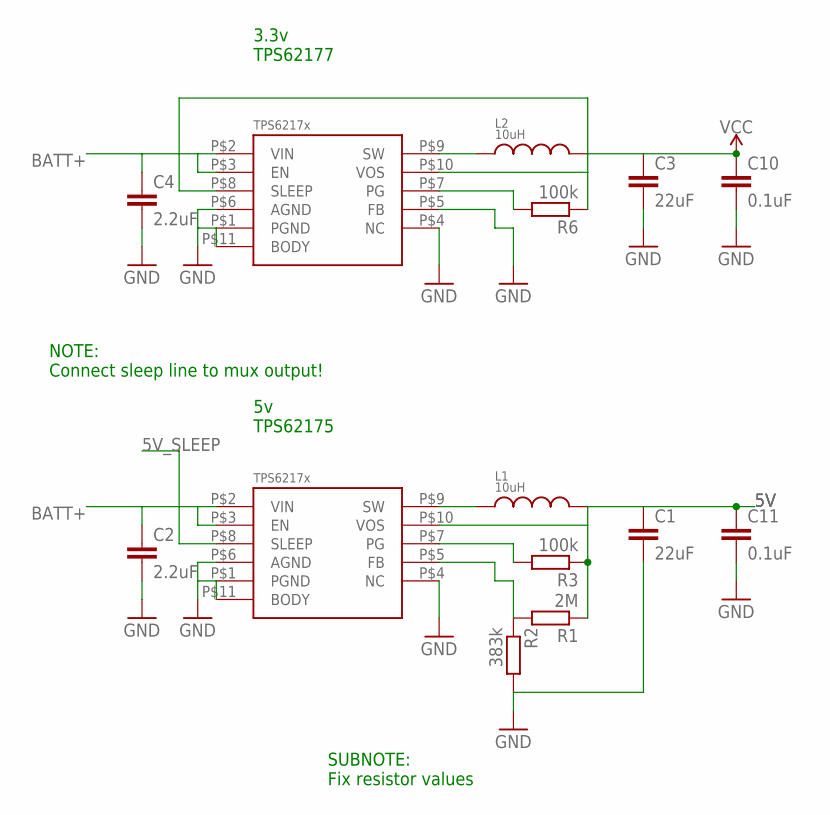
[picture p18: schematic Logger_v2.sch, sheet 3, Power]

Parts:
C1, C3: 22uF; C1210
C2, C4: 2.2uF; C0603
C10, C11: 0.1uF; C0603
L1, L2: 10uH; WE-LQS(INDUCTOR)
R1: 2M; R0603
R2: 383k; R0603
R3, R6: 100k; R0603
U$3, U$4: TPS6217X; WSON-10

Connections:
3.3V: C3.1, C10.1, L2.P$2, R6.1, U$4.P$8 (SLEEP), U$4.P$10 (VOS); also elsewhere on the board
5V: C1.1, C11.1, L1.P$2, R1.1, R3.1, U$3.P$10 (VOS); also elsewhere on the board
5V_SLEEP: U$3.P$8 (SLEEP)
BATT+: C2.1, C4.1, U$3.P$2 (VIN), U$3.P$3 (EN), U$4.P$2 (VIN), U$4.P$3 (EN); also elsewhere on the board
GND: C1.2, C2.2, C3.2, C4.2, C10.2, C11.2, R2.2, U$3.P$1 (PGND), U$3.P$4 (NC), U$3.P$6 (AGND), U$3.P$11 (BODY), U$4.P$1 (PGND), U$4.P$4 (NC), U$4.P$5 (FB), U$4.P$6 (AGND), U$4.P$11 (BODY); also elsewhere on the board
unnamed: L1.P$1, U$3.P$9 (SW)
unnamed: L2.P$1, U$4.P$9 (SW)
unnamed: R1.2, R2.1, U$3.P$5 (FB)
unnamed: R3.2, U$3.P$7 (PG)
unnamed: R6.2, U$4.P$7 (PG)

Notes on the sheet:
3.3v TPS62177
5v TPS62175
NOTE: Connect sleep line to mux output!
SUBNOTE: Fix resistor values

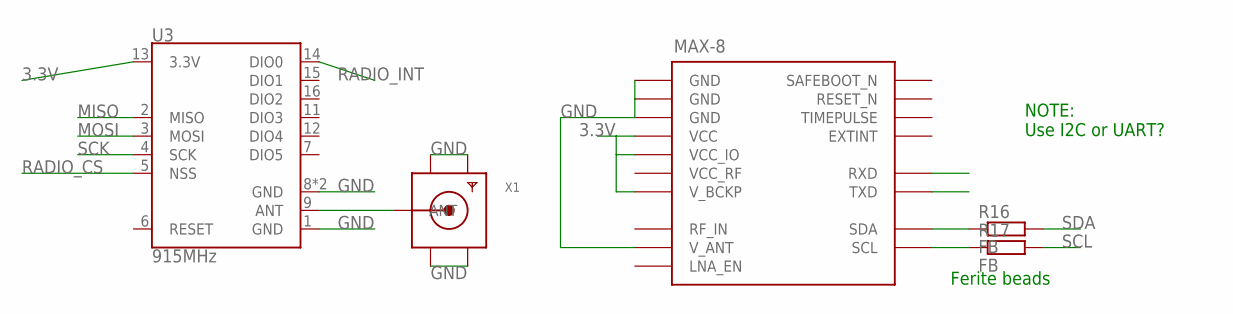
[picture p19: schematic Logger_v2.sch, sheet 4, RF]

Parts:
R16, R17: FB; R0603
U3: 915MHz; RFM69HCW-XXXS2
U$6: UBLOX_MAX-8; MAX-8
X1: SMACONNECTOR_EDGE; SMA_EDGELAUNCH

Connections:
3.3V: U3.13 (3.3V), U$6.P$6 (V_BCKP), U$6.P$7 (VCC_IO), U$6.P$8 (VCC); also elsewhere on the board
GND: U3.1 (GND), U3.8 (GND), U3.10 (GND), U$6.P$1 (GND), U$6.P$10 (GND), U$6.P$12 (GND), U$6.P$15 (V_ANT), X1.GND@1 (GND4), X1.GND@2 (GND3), X1.GND@3 (GND2), X1.GND@4 (GND1); also elsewhere on the board
MISO: U3.2 (MISO); also elsewhere on the board
MOSI: U3.3 (MOSI); also elsewhere on the board
unnamed: R16.1, U$6.P$16 (SDA)
unnamed: R17.1, U$6.P$17 (SCL)
unnamed: U3.9 (ANT), X1.P (ANT)
RADIO_CS: U3.5 (NSS); also elsewhere on the board
RADIO_INT: U3.14 (DIO0); also elsewhere on the board
SCK: U3.4 (SCK); also elsewhere on the board
SCL: R17.2; also elsewhere on the board
SDA: R16.2; also elsewhere on the board
VCC_RF: U$6.P$14 (VCC_RF)

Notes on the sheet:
NOTE: Use I2C or UART?
Ferite beads

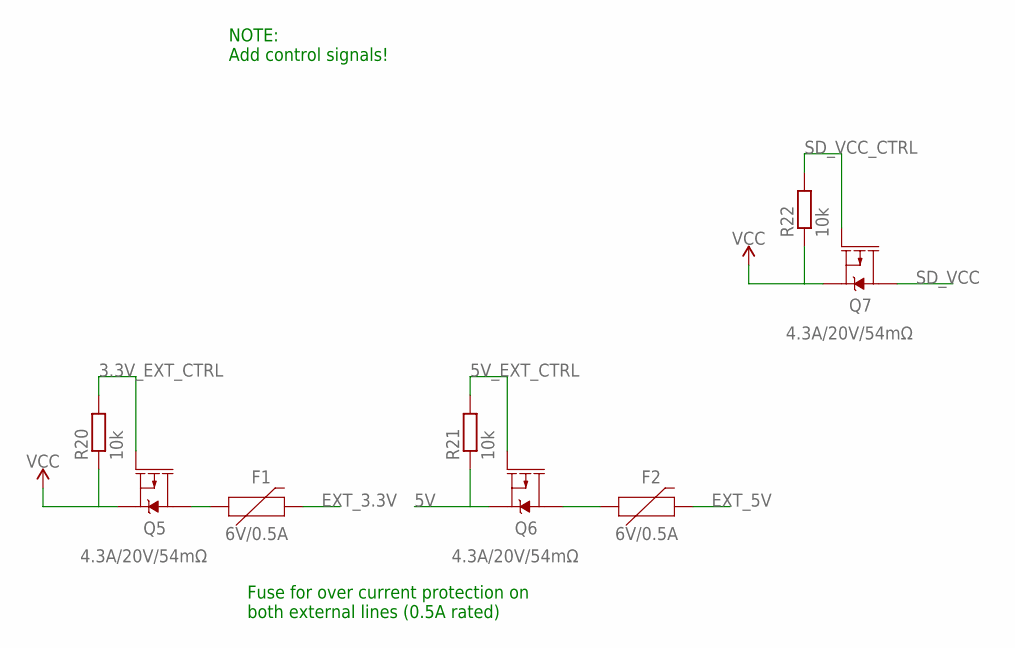
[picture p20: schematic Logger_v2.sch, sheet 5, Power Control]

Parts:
F1, F2: 6V/0.5A; 1206
Q5, Q6, Q7: 4.3A/20V/54mΩ; SOT23-3
R20, R21, R22: 10k; R0603

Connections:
3.3V: Q5.2 (S), Q7.2 (S), R20.1, R22.1; also elsewhere on the board
3.3V_EXT_CTRL: Q5.1 (G), R20.2; also elsewhere on the board
5V: Q6.2 (S), R21.1; also elsewhere on the board
5V_EXT_CTRL: Q6.1 (G), R21.2; also elsewhere on the board
EXT_3.3V: F1.2; also elsewhere on the board
EXT_5V: F2.2; also elsewhere on the board
unnamed: F1.1, Q5.3 (D)
unnamed: F2.1, Q6.3 (D)
SD_VCC: Q7.3 (D); also elsewhere on the board
SD_VCC_CTRL: Q7.1 (G), R22.2; also elsewhere on the board

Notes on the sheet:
NOTE: Add control signals!
Fuse for over current protection on both external lines (0.5A rated)

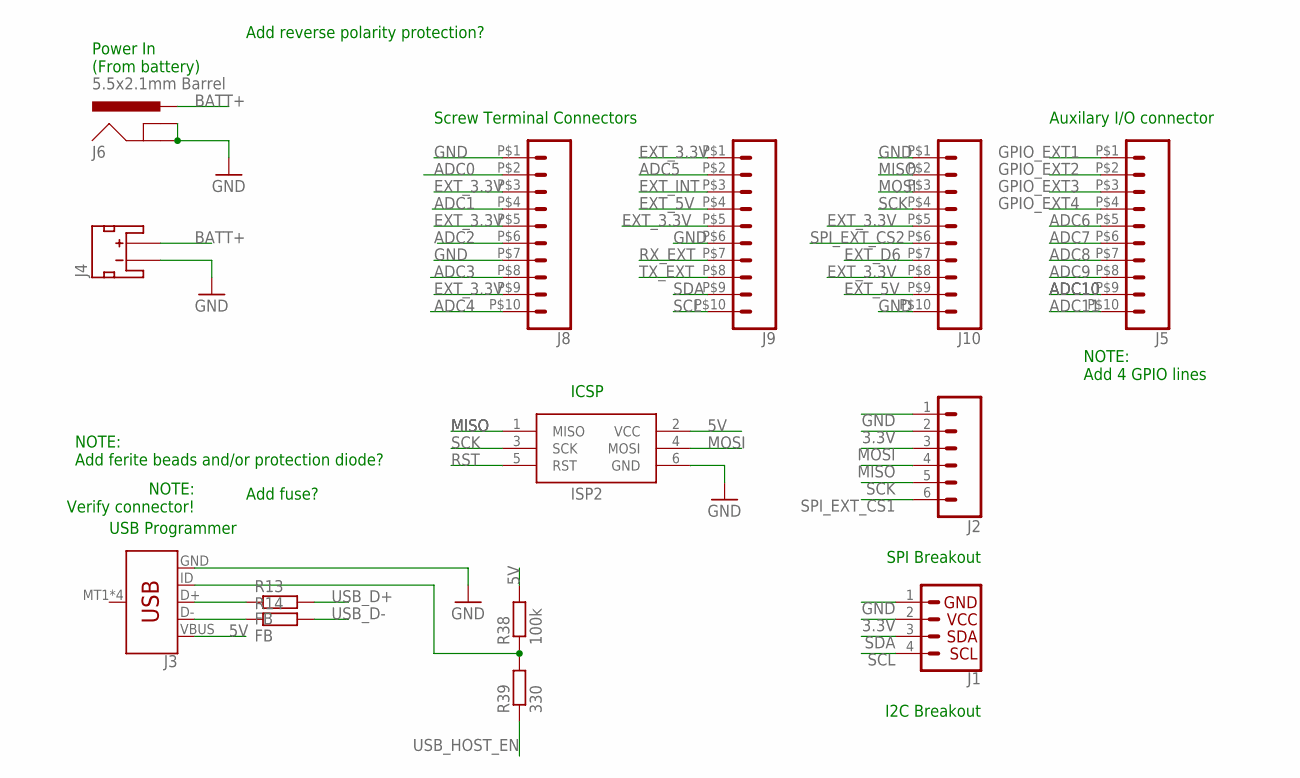
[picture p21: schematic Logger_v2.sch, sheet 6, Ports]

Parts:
ISP2: AVRISP-6; AVRISP
J1: I2C_STANDARD; 1X04
J2: CONN_06SILK_FEMALE_PTH; 1X06
J3: USB_MICRO-B_SMT; USB-MICROB
J4: JST_2MM_MALE; JST-2-SMD
J5, J8, J9, J10: CONN_10; SCREWTERMINAL-3.5MM-10
J6: 5.5x2.1mm Barrel; POWER_JACK_SMD
R13, R14: FB; R0603
R38: 100k; R0603
R39: 330; R0603

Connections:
3.3V: J1.2, J2.2; also elsewhere on the board
5V: ISP2.2 (VCC), J3.VBUS, R38.2; also elsewhere on the board
ADC0: J8.P$2 (2); also elsewhere on the board
ADC1: J8.P$4 (4); also elsewhere on the board
ADC2: J8.P$6 (6); also elsewhere on the board
ADC3: J8.P$8 (8); also elsewhere on the board
ADC4: J8.P$10 (10); also elsewhere on the board
ADC5: J9.P$2 (2); also elsewhere on the board
ADC6: J5.P$5 (5); also elsewhere on the board
ADC7: J5.P$6 (6); also elsewhere on the board
ADC8: J5.P$7 (7); also elsewhere on the board
ADC9: J5.P$8 (8); also elsewhere on the board
ADC10: J5.P$9 (9); also elsewhere on the board
ADC11: J5.P$10 (10); also elsewhere on the board
BATT+: J4.2 (+), J6.VIN0 (PWR); also elsewhere on the board
EXT_3.3V: J8.P$3 (3), J8.P$5 (5), J8.P$9 (9), J9.P$1 (1), J9.P$5 (5), J10.P$5 (5), J10.P$8 (8); also elsewhere on the board
EXT_5V: J9.P$4 (4), J10.P$9 (9); also elsewhere on the board
EXT_D6: J10.P$7 (7); also elsewhere on the board
EXT_INT: J9.P$3 (3); also elsewhere on the board
GND: ISP2.6 (GND), J1.1, J2.1, J3.GND, J4.1 (-), J6.GND (GNDBREAK), J6.P$4 (GND), J8.P$1 (1), J8.P$7 (7), J9.P$6 (6), J10.P$1 (1), J10.P$10 (10); also elsewhere on the board
GPIO_EXT1: J5.P$1 (1); also elsewhere on the board
GPIO_EXT2: J5.P$2 (2); also elsewhere on the board
GPIO_EXT3: J5.P$3 (3); also elsewhere on the board
GPIO_EXT4: J5.P$4 (4); also elsewhere on the board
MISO: ISP2.1 (MISO), J2.4, J10.P$2 (2); also elsewhere on the board
MOSI: ISP2.4 (MOSI), J2.3, J10.P$3 (3); also elsewhere on the board
unnamed: J3.D+, R13.1
unnamed: J3.D-, R14.1
unnamed: J3.ID, R38.1, R39.2
RST: ISP2.5 (RST); also elsewhere on the board
RX_EXT: J9.P$7 (7); also elsewhere on the board
SCK: ISP2.3 (SCK), J2.5, J10.P$4 (4); also elsewhere on the board
SCL: J1.4, J9.P$10 (10); also elsewhere on the board
SDA: J1.3, J9.P$9 (9); also elsewhere on the board
SPI_EXT_CS1: J2.6; also elsewhere on the board
SPI_EXT_CS2: J10.P$6 (6); also elsewhere on the board
TX_EXT: J9.P$8 (8); also elsewhere on the board
USB_D+: R13.2; also elsewhere on the board
USB_D-: R14.2; also elsewhere on the board
USB_HOST_EN: R39.1; also elsewhere on the board

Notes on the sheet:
Power In (From battery)
Add reverse polarity protection?
I2C Breakout
SPI Breakout
NOTE: Verify connector!
Add fuse?
NOTE: Add ferite beads and/or protection diode?
Screw Terminal Connectors
ICSP
USB Programmer
Auxilary I/O connector
NOTE: Add 4 GPIO lines

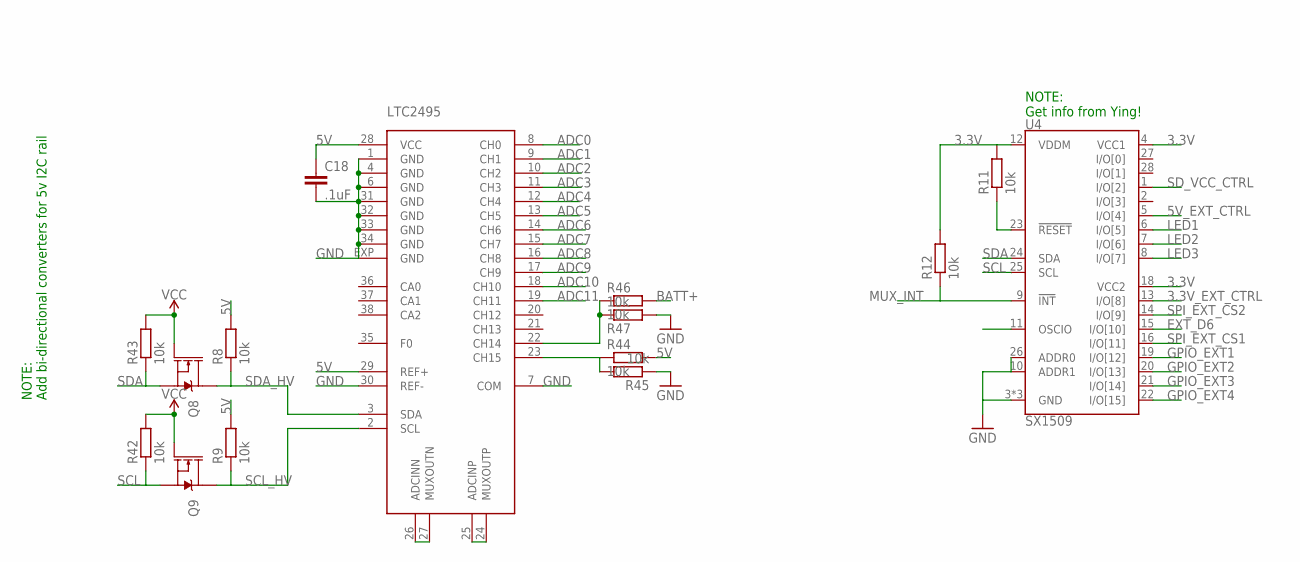
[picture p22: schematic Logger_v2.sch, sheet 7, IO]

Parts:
C18: .1uF; C0603
Q8, Q9: 220mA/50V/3.5Ω; SOT23-3
R8, R9, R11, R12, R42, R43, R44, R45, R46, R47: 10k; R0603
U4: SX1509; QFN-28
U$7: LTC2495; QFN38-5X7

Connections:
3.3V: Q8.1 (G), Q9.1 (G), R11.2, R12.2, R42.2, R43.2, U4.4 (VCC1), U4.12 (VDDM), U4.18 (VCC2); also elsewhere on the board
3.3V_EXT_CTRL: U4.13 (I/O[8]); also elsewhere on the board
5V: C18.1, R8.2, R9.2, R44.2, U$7.28 (VCC), U$7.29 (REF+); also elsewhere on the board
5V_EXT_CTRL: U4.5 (I/O[4]); also elsewhere on the board
ADC0: U$7.8 (CH0); also elsewhere on the board
ADC1: U$7.9 (CH1); also elsewhere on the board
ADC2: U$7.10 (CH2); also elsewhere on the board
ADC3: U$7.11 (CH3); also elsewhere on the board
ADC4: U$7.12 (CH4); also elsewhere on the board
ADC5: U$7.13 (CH5); also elsewhere on the board
ADC6: U$7.14 (CH6); also elsewhere on the board
ADC7: U$7.15 (CH7); also elsewhere on the board
ADC8: U$7.16 (CH8); also elsewhere on the board
ADC9: U$7.17 (CH9); also elsewhere on the board
ADC10: U$7.18 (CH10); also elsewhere on the board
ADC11: U$7.19 (CH11); also elsewhere on the board
BATT+: R46.2; also elsewhere on the board
EXT_D6: U4.15 (I/O[10]); also elsewhere on the board
GND: C18.2, R45.1, R47.2, U4.3 (GND), U4.10 (ADDR1), U4.17 (GND), U4.26 (ADDR0), U4.29 (GND), U$7.1 (GND), U$7.4 (GND), U$7.6 (GND), U$7.7 (COM), U$7.30 (REF-), U$7.31 (GND), U$7.32 (GND), U$7.33 (GND), U$7.34 (GND), U$7.EXP (GND); also elsewhere on the board
GPIO_EXT1: U4.19 (I/O[12]); also elsewhere on the board
GPIO_EXT2: U4.20 (I/O[13]); also elsewhere on the board
GPIO_EXT3: U4.21 (I/O[14]); also elsewhere on the board
GPIO_EXT4: U4.22 (I/O[15]); also elsewhere on the board
LED1: U4.6 (I/O[5]); also elsewhere on the board
LED2: U4.7 (I/O[6]); also elsewhere on the board
LED3: U4.8 (I/O[7]); also elsewhere on the board
MUX_INT: R12.1, U4.9 (!INT); also elsewhere on the board
unnamed: U$7.26 (ADCINN), U$7.27 (MUXOUTN)
unnamed: U$7.24 (MUXOUTP), U$7.25 (ADCINP)
unnamed: R44.1, R45.2, U$7.23 (CH15)
unnamed: R46.1, R47.1, U$7.22 (CH14)
unnamed: R11.1, U4.23 (!RESET)
SCL: Q9.2 (S), R42.1, U4.25 (SCL); also elsewhere on the board
SCL_HV: Q9.3 (D), R9.1, U$7.2 (SCL)
SDA: Q8.2 (S), R43.1, U4.24 (SDA); also elsewhere on the board
SDA_HV: Q8.3 (D), R8.1, U$7.3 (SDA)
SD_VCC_CTRL: U4.1 (I/O[2]); also elsewhere on the board
SPI_EXT_CS1: U4.16 (I/O[11]); also elsewhere on the board
SPI_EXT_CS2: U4.14 (I/O[9]); also elsewhere on the board

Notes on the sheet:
NOTE: Add bi-directional converters for 5v I2C rail
NOTE: Get info from Ying!

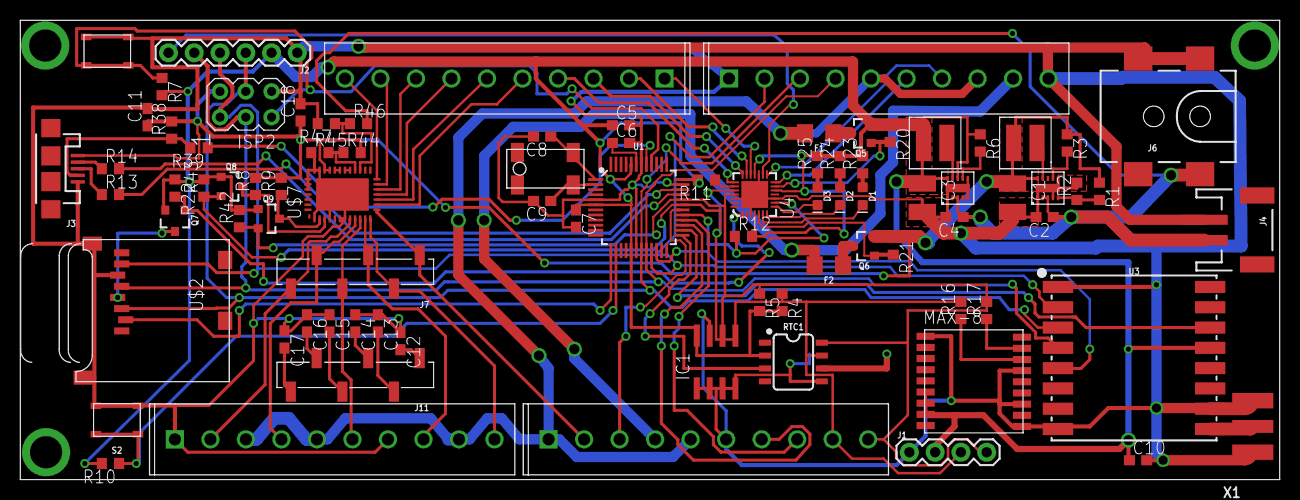
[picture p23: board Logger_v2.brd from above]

Board: 2 copper layers, 124.1 x 45.3 mm, 87 parts (1 on the bottom side), 83 nets.

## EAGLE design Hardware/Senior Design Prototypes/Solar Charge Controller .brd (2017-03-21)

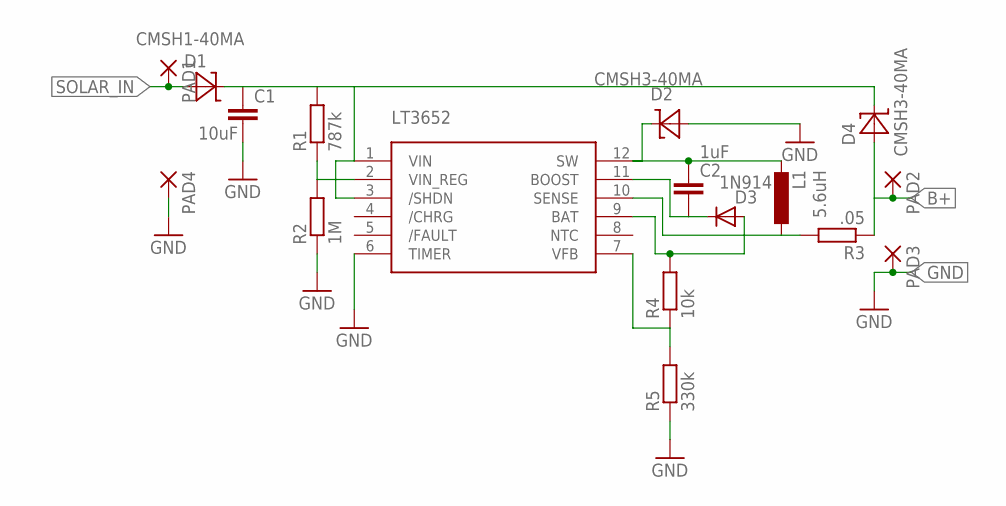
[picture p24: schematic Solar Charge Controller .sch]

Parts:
C1: 10uF; C0805
C2: 1uF; C0603
D1: CMSH1-40MA; DO-214AC
D2, D4: CMSH3-40MA; DO-214AC
D3: 1N914; SOD523
L1: 5.6uH; 1008(2510METRIC)
PAD1, PAD2, PAD3, PAD4: SMD5; SMD2,54-5,08
R1: 787k; R0603
R2: 1M; R0603
R3: .05; R0805
R4: 10k; R0603
R5: 330k; R0603
U$1: LT3652; MSOP12

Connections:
B+: D4.A, PAD2.1, R3.1
GND: C1.2, D2.A, PAD3.1, PAD4.1, R2.1, R5.1, U$1.6 (TIMER)
unnamed: C1.1, D1.C, D4.C, R1.2, U$1.1 (VIN), U$1.3 (/SHDN)
unnamed: R1.1, R2.2, U$1.2 (VIN_REG)
unnamed: C2.1, D2.C, L1.P$3 (2), U$1.12 (SW)
unnamed: L1.P$2 (1), R3.2, U$1.10 (SENSE)
unnamed: D3.A, R4.2, U$1.9 (BAT)
unnamed: C2.2, D3.C, U$1.11 (BOOST)
unnamed: R4.1, R5.2, U$1.7 (VFB)
SOLAR_IN: D1.A, PAD1.1

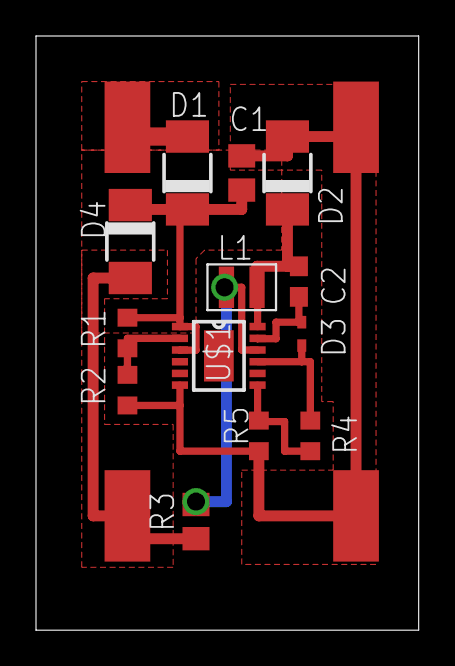
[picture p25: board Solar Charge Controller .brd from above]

Board: 2 copper layers, 21.3 x 33.0 mm, 17 parts (0 on the bottom side), 10 nets.

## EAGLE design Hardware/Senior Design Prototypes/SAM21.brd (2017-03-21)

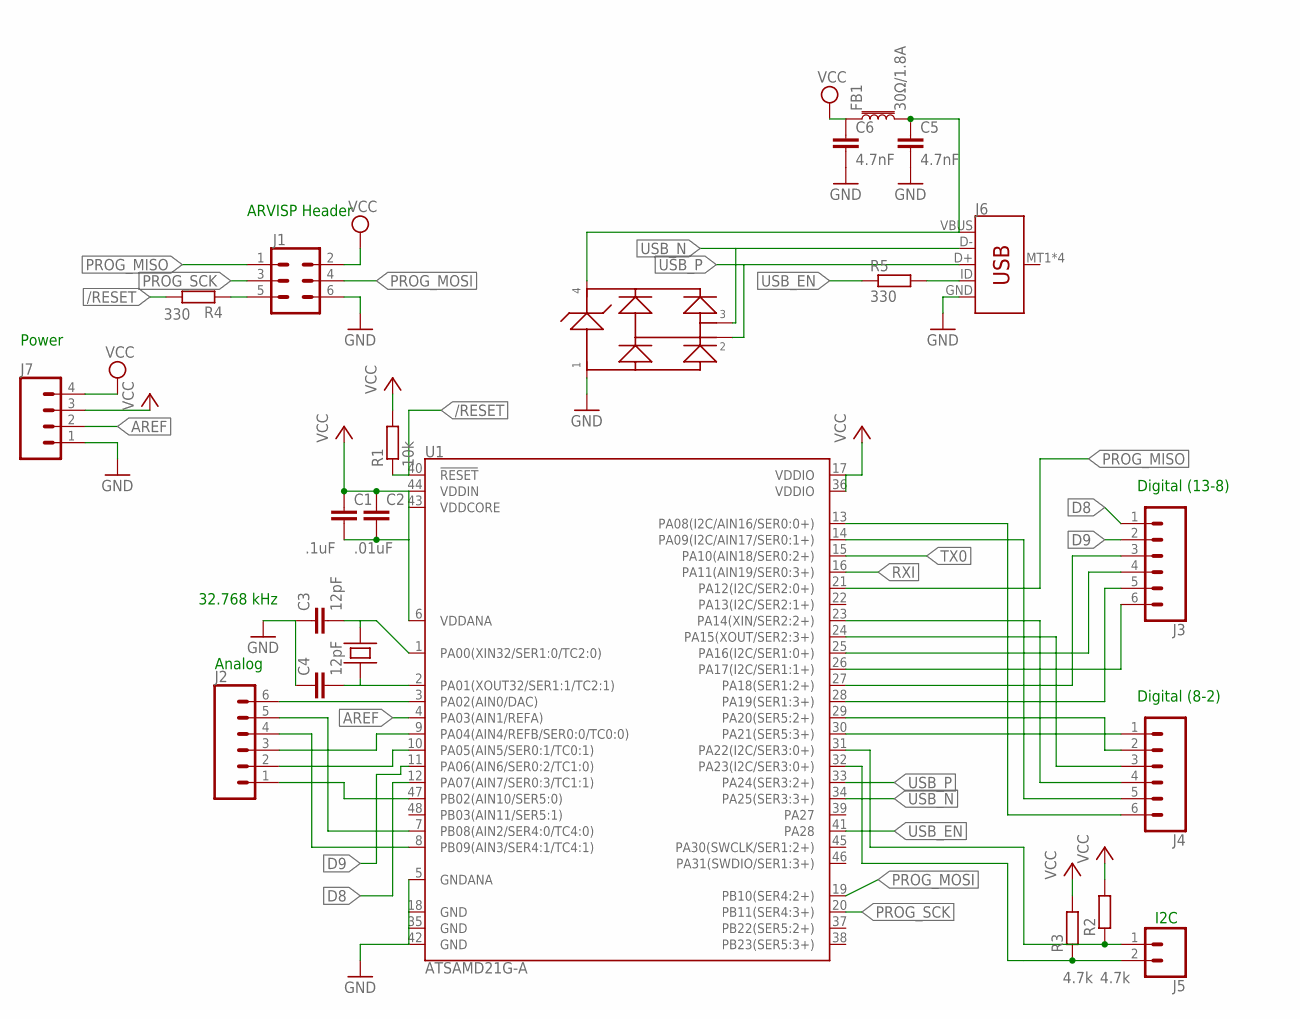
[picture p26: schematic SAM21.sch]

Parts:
C1: .1uF; C0603
C2: .01uF; C0603
C3, C4: 12pF; C0603
C5, C6: 4.7nF; C0603
FB1: 30Ω/1.8A; 0603
J1: CONN_03X2FEMALE_SMD; 2X3_SMD
J2, J3, J4: CONN_06LONGPADS; 1X06_LONGPADS
J5: CONN_02PTH3; 1X02_LONGPADS
J6: USB_MICRO-B_SMT; USB-MICROB
J7: CONN_04LONGPADS; 1X04_LONGPADS
R1: 10k; R0603
R2, R3: 4.7k; R0603
R4, R5: 330; R0603
U1: ATSAMD21G-A; TQFP-48
U$1: CM200; 4-SOJ
U$2: PRTR5V0U2X; SOT143B

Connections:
5V: J1.2
/RESET: R1.1, R4.2, U1.40 (!RESET!)
AREF: J7.2, U1.4 (PA03(AIN1/REFA))
D8: J3.1, U1.12 (PA07(AIN7/SER0:3/TC1:1))
D9: J2.4, J3.2, U1.8 (PB09(AIN3/SER4:1/TC4:1)), U1.11 (PA06(AIN6/SER0:2/TC1:0))
GND: C3.1, C4.1, C5.2, C6.2, J1.6, J6.GND, J7.1, U1.5 (GNDANA), U1.18 (GND), U1.35 (GND), U1.42 (GND), U$2.P$1 (1)
unnamed: J4.1, U1.30 (PA21(SER5:3+))
unnamed: J2.6, U1.3 (PA02(AIN0/DAC))
unnamed: J2.5, U1.7 (PB08(AIN2/SER4:0/TC4:0))
unnamed: J4.2, U1.29 (PA20(SER5:2+))
unnamed: J2.3, U1.9 (PA04(AIN4/REFB/SER0:0/TC0:0))
unnamed: J2.2, U1.10 (PA05(AIN5/SER0:1/TC0:1))
unnamed: J2.1, U1.47 (PB02(AIN10/SER5:0))
unnamed: J3.6, U1.26 (PA17(I2C/SER1:1+))
unnamed: J3.5, U1.28 (PA19(SER1:3+))
unnamed: J3.4, U1.25 (PA16(I2C/SER1:0+))
unnamed: J3.3, U1.27 (PA18(SER1:2+))
unnamed: J4.3, U1.24 (PA15(XOUT/SER2:3+))
unnamed: J4.4, U1.23 (PA14(XIN/SER2:2+))
unnamed: J4.5, U1.14 (PA09(I2C/AIN17/SER0:1+))
unnamed: J4.6, U1.13 (PA08(I2C/AIN16/SER0:0+))
unnamed: U1.17 (VDDIO), U1.36 (VDDIO)
unnamed: J5.1, R2.1, U1.31 (PA22(I2C/SER3:0+))
unnamed: C4.2, U1.2 (PA01(XOUT32/SER1:1/TC2:1)), U$1.P$1
unnamed: J5.2, R3.1, U1.32 (PA23(I2C/SER3:0+))
unnamed: J1.5, R4.1
unnamed: C3.2, U1.1 (PA00(XIN32/SER1:0/TC2:0)), U$1.P$4
unnamed: C5.1, FB1.2, J6.VBUS, U$2.P$4 (4)
unnamed: J6.ID, R5.2
PROG_MISO: J1.1, U1.21 (PA12(I2C/SER2:0+))
PROG_MOSI: J1.4, U1.19 (PB10(SER4:2+))
PROG_SCK: J1.3, U1.20 (PB11(SER4:3+))
RXI: U1.16 (PA11(AIN19/SER0:3+))
TX0: U1.15 (PA10(AIN18/SER0:2+))
USB_EN: R5.1, U1.41 (PA28)
USB_N: J6.D-, U1.34 (PA25(SER3:3+)), U$2.P$3 (3)
USB_P: J6.D+, U1.33 (PA24(SER3:2+)), U$2.P$2 (2)
VCC: C1.1, C1.2, C2.1, C2.2, C6.1, FB1.1, J7.3, J7.4, R1.2, R2.2, R3.2, U1.6 (VDDANA), U1.43 (VDDCORE), U1.44 (VDDIN)

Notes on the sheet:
ARVISP Header
Analog
Digital (13-8)
Digital (8-2)
I2C
32.768 kHz
Power

Board: 2 copper layers, 22 parts (0 on the bottom side), 35 nets, no tracks yet.

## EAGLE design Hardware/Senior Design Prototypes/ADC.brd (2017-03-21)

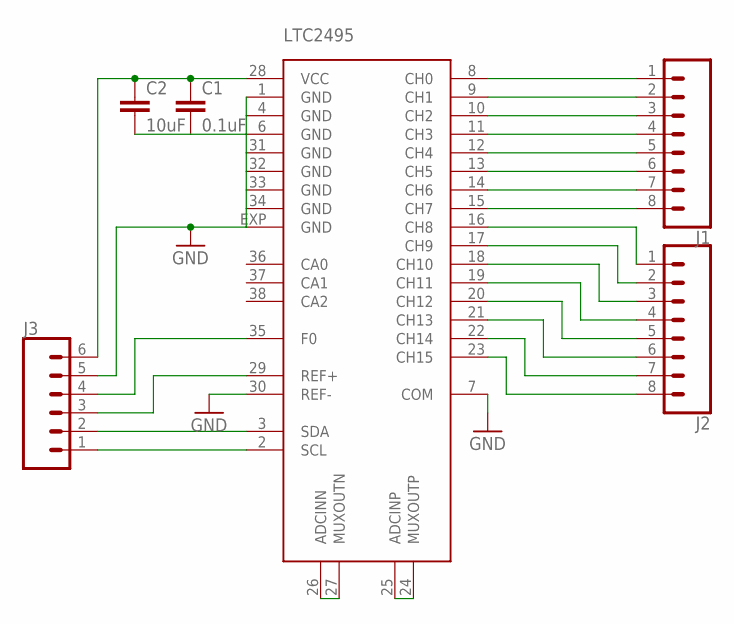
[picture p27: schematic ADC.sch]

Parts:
C1: 0.1uF; C0603
C2: 10uF; C0805
J1, J2: CONN_08LONGPADS; 1X08_LONGPADS
J3: CONN_06LONGPADS; 1X06_LONGPADS
U$1: LTC2495; QFN38-5X7

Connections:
GND: C1.2, C2.2, J3.5, U$1.1 (GND), U$1.4 (GND), U$1.6 (GND), U$1.7 (COM), U$1.30 (REF-), U$1.31 (GND), U$1.32 (GND), U$1.33 (GND), U$1.34 (GND), U$1.EXP (GND)
unnamed: J3.1, U$1.2 (SCL)
unnamed: J3.2, U$1.3 (SDA)
unnamed: J3.3, U$1.29 (REF+)
unnamed: J3.4, U$1.35 (F0)
unnamed: C1.1, C2.1, J3.6, U$1.28 (VCC)
unnamed: U$1.26 (ADCINN), U$1.27 (MUXOUTN)
unnamed: U$1.24 (MUXOUTP), U$1.25 (ADCINP)
unnamed: J1.8, U$1.15 (CH7)
unnamed: J1.7, U$1.14 (CH6)
unnamed: J1.6, U$1.13 (CH5)
unnamed: J1.5, U$1.12 (CH4)
unnamed: J1.4, U$1.11 (CH3)
unnamed: J1.3, U$1.10 (CH2)
unnamed: J1.2, U$1.9 (CH1)
unnamed: J1.1, U$1.8 (CH0)
unnamed: J2.1, U$1.16 (CH8)
unnamed: J2.2, U$1.17 (CH9)
unnamed: J2.3, U$1.18 (CH10)
unnamed: J2.4, U$1.19 (CH11)
unnamed: J2.5, U$1.20 (CH12)
unnamed: J2.6, U$1.21 (CH13)
unnamed: J2.7, U$1.22 (CH14)
unnamed: J2.8, U$1.23 (CH15)


Board: 2 copper layers, 26.3 x 40.6 mm, 6 parts (0 on the bottom side), 24 nets.

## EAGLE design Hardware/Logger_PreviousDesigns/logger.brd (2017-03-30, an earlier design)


Board: 2 copper layers, 99.0 x 44.1 mm, 73 parts (0 on the bottom side), 60 nets.

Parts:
3V3: 6-TMLF
5V_CHARGE_PUMP: 5V; SON65P200X200X80-7N
A0, A1, A2, A3, A6, A7: 0207/10
ADECOUP: 0.1uF; C0603
C1, C17: 0.1uF; C0603
C14, C15: 10nF; CECJ-1206
C21: 10uF; EIA3216
CLOCK_BATT: 3V Backup Battery; BATTCON_12MM_PTH
CLOCK_BATT_DECOUP: 0.1uF; C0603
CLOCK_BATT_DECOUPLE: 10uF; EIA3216
CLOCK_CIN1, CLOCK_CIN2, CLOCK_CIN3: 1uF; C0603
CN1: JST-PH-2-THM
COUT: 1uF; C0603
COUT1: 0.1uF; C0603
CX0, CX1, CX2, CX3: 33pF; C0603
C_BOOST_1: 4.7uF; C0603
C_BOOST_2, C_BOOST_3: 2.2uF; C0603
D1: BAT54C; SOT23C
D2: BAT54; SOT23C
D+: 27ohm; R0603
D-: 27ohm; R0603
H0, H1, H3: SCREWTERMINAL-3.5MM-8
IC1: LTC4412; TSOT23-6
ISP: AVRISP-6; AVRISP
J1: POWER_JACKPTH; POWER_JACK_PTH
JP1, JP2, JP3, JP4: STAND-OFF
JP5: USB-B; USB-B-PTH
LED: LED3MM
LED1: Yellow; LED-0603
LED2: Blue; LED-0603
LOG: LOG; TACTILE-PTH
LOGO1: OSHW-LOGOM; OSHW-LOGO-M
LSHIFT: 4050D; SO16
L_LPF: 10uH; 0805
MCU: ATMEGA328P-MU; QFN50P500X500X100-33N
Q1, Q2: FDN360P; SUPER-SOT3
Q3, Q4: 2N7002PW; SOT323
RCKL1: 220; R0603
RCLK2: 220; R0603
RESET: Reset; TACTILE-PTH
RN1: 1K; 0603-ARC
RN2: 3.3K; 0603-ARC
RSTAT: 470k; R0603
R_LED: 220; R0603
R_RESET: 10k; R0603
SD: SDMMC06132; 06132
U1: DS3231MZ/V+T; 21-0041B_8
U2: FT231X-Q; QFN20
U$1: NWLOGO
U$2: ALOG_LOGO_V1_5.5MM; ALOG_LOGO_V1_SMALL
U$3: NWLOGO_MED
U$9: ALOG-BACKSILK-2.0
XTAL: 8MHz; HC49U-V

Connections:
5V: 5V_CHARGE_PUMP.3, C_BOOST_3.2, H1.4, H3.9
+3V3: 3V3.1, CLOCK_CIN2.1, H0.3, H0.5, H0.9, H1.1, H3.8, MCU.20
A0: A0.2, C14.C1, H0.2, MCU.23
A1: A1.2, C14.D1, H0.4, MCU.24
A2: A2.2, C15.A1, H0.6, MCU.25
A3: A3.2, C15.B1, H0.8, MCU.26
A6: A6.1, C15.C1, H0.10, MCU.19
A7: A7.1, C15.D1, H1.2, MCU.22
AVCC: ADECOUP.1, L_LPF.2, MCU.18
BAT: CLOCK_BATT_DECOUP.1, CLOCK_BATT_DECOUPLE.A, D1.3, U1.6
CLK: H3.4, ISP.3, LSHIFT.3, MCU.17
CS-SD: LSHIFT.7, MCU.14
D3-INT1: H1.3, MCU.1
D4-SENSE_LDO_SWITCH: 3V3.4, 5V_CHARGE_PUMP.6, MCU.2
D5_MANUAL_LOG: D2.2, MCU.9
D6-EXT: H3.7, MCU.10
D7-CLOCK_SD_SWITCH: 3V3.3, MCU.11
D8_LED: MCU.12, R_LED.1
D9-CS-EXT: H3.6, MCU.13
DI: H3.2, ISP.4, LSHIFT.5, MCU.15
DO: H3.3, ISP.1, MCU.16, SD.7
DTR: COUT1.1, U2.18
GND: 3V3.5, 5V_CHARGE_PUMP.1, 5V_CHARGE_PUMP.7, A0.1, A1.1, A2.1, A3.1, A6.2, A7.2, ADECOUP.2, C1.2, C14.A2, C14.B2, C14.C2, C14.D2, C15.A2, C15.B2, C15.C2, C15.D2, C17.2, C21.C, CLOCK_BATT.GND, CLOCK_BATT_DECOUP.2, CLOCK_BATT_DECOUPLE.C, CLOCK_CIN1.2, CLOCK_CIN2.2, CLOCK_CIN3.2, CN1.2, COUT.2, CX0.1, CX1.1, CX2.1, CX3.1, C_BOOST_1.1, C_BOOST_3.1, H0.1, H0.7, H1.6, H3.1, H3.10, IC1.2, IC1.3, ISP.6, J1.GND, J1.GNDBREAK, JP5.GND, LED.K, LOG.1, LSHIFT.8, LSHIFT.9, LSHIFT.11, LSHIFT.14, MCU.3, MCU.5, MCU.21, MCU.33, RESET.1, SD.3, SD.6, SD.GP, SD.GP3, U1.5, U2.3, U2.6, U2.13, U2.21
INT0: D2.1, MCU.32, U1.3
LED+: LED.A, R_LED.2
unnamed: D1.1, RCLK2.1
unnamed: CLOCK_BATT.VCC@1, RCLK2.2
unnamed: CX3.2, D+.2, JP5.D+
unnamed: CX2.2, D-.2, JP5.D-
unnamed: LED2.A, RN1.4
unnamed: LED2.C, U2.7
unnamed: IC1.4, Q2.1, RSTAT.1
unnamed: IC1.5, Q1.1
unnamed: LED1.A, RN1.3
unnamed: LED1.C, U2.14
unnamed: D2.3, LOG.3
unnamed: D-.1, U2.9
unnamed: 5V_CHARGE_PUMP.4, C_BOOST_2.2
unnamed: 5V_CHARGE_PUMP.5, C_BOOST_2.1
unnamed: D+.1, U2.8
unnamed: C1.1, U2.10, U2.11, U2.20
unnamed: RN1.1, U2.17
unnamed: RN1.2, U2.1
unnamed: D1.2, RCKL1.1
RESET: COUT1.2, ISP.5, MCU.29, RESET.3, R_RESET.1
RX-I: H1.7, MCU.30, RN1.8
SCL: H1.10, MCU.28, Q4.3, RN2.7
SCL_3V3: Q4.2, RN2.3, U1.8
SDA: H1.9, MCU.27, Q3.3, RN2.8
SDA_3V3: Q3.2, RN2.4, U1.7
SD_CLK: LSHIFT.2, SD.5
SD_CS: LSHIFT.6, SD.1
SD_DI: LSHIFT.4, SD.2
TX-O: H1.8, MCU.31, RN1.7
VBAT: CN1.1, IC1.1, J1.PWR, Q1.3
VCC: 3V3.6, 5V_CHARGE_PUMP.2, C14.A1, CLOCK_CIN1.1, COUT.1, C_BOOST_1.2, H1.5, H3.5, IC1.6, ISP.2, L_LPF.1, MCU.4, MCU.6, Q1.2, Q2.2, RCKL1.2, RN2.1, RN2.2, RSTAT.2, R_RESET.2
VDD: 3V3.2, C14.B1, CLOCK_CIN3.1, LSHIFT.1, Q3.1, Q4.1, RN2.5, RN2.6, SD.4, U1.2
VUSB: C17.1, C21.A, JP5.VBUS, Q2.3, RN1.5, RN1.6, U2.12
X0: CX0.2, MCU.7, XTAL.2
X1: CX1.2, MCU.8, XTAL.1

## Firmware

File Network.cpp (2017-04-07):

/*
 * =====================================================================================
 *
 *       Filename:  Network.cpp
 *
 *    Description:  Protocol used for radio communication using the ALogger
 *
 *        Version:  1.0
 *        Created:  02/01/2017 11:26:22 AM
 *       Revision:  none
 *       Compiler:  gcc
 *
 *         Author:  Luke Cesarz, Jeff Worm, David Nickel, Robert Schulz, Ying
 *                  Yang
 *     University:  University of Minnesota TC
 *
 * =====================================================================================
 *
## LICENSE: GNU GPL v3

Network.h is part of Logger, an Arduino library written by Andrew D. Wickert
and Chad T. Sandell.

Copyright (C) 2011-2015, Andrew D. Wickert<br>
Copyright (C) 2016, Andrew D. Wickert and Chad T. Sandell

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
You should have received a copy of the GNU General Public License
along with this program.  If not, see <http://www.gnu.org/licenses/>.
*/
#include <Network.h>

//Default Constructor
void Network::Network() {}

retVal Network::initNetwork(uint8_t networkID)
{
    //TODO: set myID from EEPROM
    //this.myID = EEPROM.read(idaddress);
    this.networkID = networkID;
    digitalWrite(radioChipSelectPin, LOW);
    //TODO: set other chip selects high
    radio.initialize(RF69_915MHZ, this.myID, this.networkID);
    radio.writeReg(0x03, 0x0A);
    radio.writeReg(0x04, 0x00);
    radio.setHighPower();
    //TODO: check usb connection and (un)set amCoord then (do nothing)broadcast i am coord
}

/* * * * * * * * * * * * * * * * * * * * * * * * * * * * * *
 * Fills a packet class object with data from a packet that
 * that has been received. Returns NOMESSAGE if there was
 * nothing to be received, or returns SUCCESS
 * * * * * * * * * * * * * * * * * * * * * * * * * * * * * */
retVal Network::readPacket(Packet* p)
{
    digitalWrite(radioChipSelectPin, LOW);
    //TODO: set other chip selects high
    if (this.radio.receiveDone()) {
        if (this.radio.ACKRequested())
            this.radio.sendACK();
        p->setdSize(this.radio.PAYLOADLEN - 1);
        p->setsAddr(this.radio.SENDERID);
        p->setdAddr(this.radio.TARGETID);
        p->setopCode(this.radio.DATA[0]);
        p->setRSSI(this.radio.readRSSI());
        for (int i = 0; i < p->getdSize(); i++) {
            p->setdata(this.radio.DATA[i + 1], i);
        }
        for (int i = p->getdSize(); i < MAXDATASIZE; i++) {
            p->setdata(0, i);
        }
        return SUCCESS;
    }
    return NOMESSAGE;
}

/* * * * * * * * * * * * * * * * * * * * * * * * * * * * * *
 * Sends the packet to the node identified by p->getdAddr()
 * * * * * * * * * * * * * * * * * * * * * * * * * * * * * */
retVal Network::sendPacket(Packet* p)
{
    digitalWrite(radioChipSelectPin, LOW);
    //TODO: set other chip selects high
    uint8_t data[p->getdSize() + 1];
    data[0] = p->getopCode();
    for (int i = 0; i < p->getdSize(); i++) {
        data[i + 1] = p->getdata(i);
    }
    if (this.useAck && p->getdAddr() != BROADCASTADDRESS) {
        if (this.radio.sendWithRetry(p->getdAddr(), data, p->getdSize() + 1)) {
            return SUCCESS;
        }
        else {
            return NOACK;
        }
    }
    else {
        this.radio.send(p->getdAddr(), data, p->getdSize() + 1);
        return SUCCESS;
    }
}

/* * * * * * * * * * * * * * * * * * * * * * * * * * * * * *
 * Fills the packet pointed to by p with the info passed in
 * * * * * * * * * * * * * * * * * * * * * * * * * * * * * */
void Network::createPacket(uint8_t opCode, uint8_t sAddr, uint8_t dAddr, uint8_t dSize, uint8_t data[], Packet* p)
{
    p->setopCode(opCode);
    p->setsAddr(sAddr);
    p->setdAddr(dAddr);
    p->setdSize(dSize);
    for (int i = 0; i < dSize; i++)
        p->setdata(data[i], i);
    for (int i = dSize; i < MAXDATASIZE; i++)
        p->setdata(0, i);
}

/* * * * * * * * * * * * * * * * * * * * * * * * * * * * * *
 * Sends a broadcast packet to the network looking for
 * the coordinator node
 * * * * * * * * * * * * * * * * * * * * * * * * * * * * * */
void Network::lookForCoord()
{
    Packet* p = new Packet();
    createPacket(ASKFORCOORD, this.myID, BROADCASTADDRESS, 0, NULL, p);
    sendPacket(p);
    delete p;
}

/* * * * * * * * * * * * * * * * * * * * * * * * * * * * * *
 * Sends a broadcast packet to the network saying that
 * we have a connection to coord
 * * * * * * * * * * * * * * * * * * * * * * * * * * * * * */
void Network::foundCoord()
{
    Packet* p = new Packet();
    createPacket(IHAVECOORD, this.myID, BROADCASTADDRESS, 0, NULL, p);
    sendPacket(p);
    delete p;
}

/* * * * * * * * * * * * * * * * * * * * * * * * * * * * * *
 * Sends a broadcast packet to the network saying that
 * we have dropped connection to coord and sets appropriate
 * variables for the loss of connection
 * * * * * * * * * * * * * * * * * * * * * * * * * * * * * */
void Network::droppedCoord(){
    this.haveCoord = false;
    this.currentRSSI = 0;
    Packet* p = new Packet();
    createPacket(DROPPEDCOORD, this.myID, BROADCASTADDRESS, 0, NULL, p);
    sendPacket(p);
    delete p;
}

void Network::runNetwork()
{
    //wake up radio
    short noPacketReceived=0;
    Packet *p = new Packet();
    if(this.amCoord){
		    //listen
        //TODO figure out these timeouts, there are infinite ways to do them,
        //but I think this way will work: have a counter on the number of times
        //a packet was not received and once it exceeds COORDLISTENTIMEOUT then
        //stop listening we also tune the sleeps accordingly.
        while(noPacketReceived < COORDLISTENTIMEOUT){
            if(readPacket(p) != NOMESSAGE){
                receivedPacket(p);
            }
            else{
                noPacketReceived++;
            }
            //TODO sleep for some amount of time. Can change the sleep time depending
            //on whether or not we received a packet.
        }
	}
	else if(this.haveCoord){
		    //send yourdata
        uint8_t data[MAXDATASIZE];
        uint8_t index;
        float d;
        while(!dataQueue.isEmpty()){
            for(index = 1 ; index<MAXDATASIZE-3 && !dataQueue.isEmpty();){
                d = dataQueue.dequeue();
                data[index++] = d >> 24;
                data[index++] = d >> 16;
                data[index++] = d >> 8;
                data[index++] = d;
            }
            uint8_t failedSend = 0;
            createPacket(DTRANSMISSION, this.myID, this.nextHop, size, data, p);
            while((sendPacket(p) == NOACK) && (failedSend < DROPPEDPACKETTIMEOUT)){
              failedSend++;
              //TODO sleep for some amount of time. (Sould we sleep or immedeately try to resend?)
            }
            if(failedSend == DROPPEDPACKETTIMEOUT){
              //handle what happens on timeout (Never get ACK'd)
              droppedCoord();
              delete p;
              //radio.sleep();
              return;
            }
        }
		    //listen forward
        bool dropped = false;
        while(noPacketReceived < ROUTERLISTENTIMEOUT){
            if(readPacket(p) != NOMESSAGE){
                if(receivedPacket(p) == DROPPED){
                  dropped = true;
                  break;
                }
            }
            else{
                noPacketReceived++;
            }
            //TODO sleep for some amount of time. Can change the sleep time depending
            //on whether or not we received a packet.
        }
        if(dropped){
          droppedCoord();
        }
	}
	else{
		    //ask for coord
        lookForCoord(); //NOTE: from Jeff, I think we should send this every so many (5 maybe? TDB) noPacketReceived
                        //incremnets in case no one was listening
		    //listen and choose best next hop
        while(noPacketReceived < LFCLISTENTIMEOUT /* && wait for multiple answers*/){
            if(readPacket(p) != NOMESSAGE){
                receivedPacket(p);
            }
            else{
                noPacketReceived++;
            }
            //TODO sleep for some amount of time. Can change the sleep time depending
            //on whether or not we received a packet.
        }
        //next best hop is selected in receivedPacket()
        //after we have listened long enough and we have
        //reconnected we can say we have coord again and
        //move on to the next round of runNetwork()
        if(this.reconnected){
          this.reconnected = false;
          this.haveCoord = true;
          foundCoord();
        }
	}
  delete p;
}
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

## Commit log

2017-02-07 radio chip library added
    [SonarMote_lasercut plans_1.75mm acrylic.dxf]
2017-02-22 Added Hardware section and moddified RFM69 Example
    Added a hardware folder and moved work from existing git hardware section into this, will move current eagle work into this section soon. Also made changes to the example file for thr RFM69
    [ALog_BottleLogger_bill_of_materials.xls, logger.GBL, logger.GBO, logger.GBS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]
2017-03-21 Added logger schematic
    Added the schematic for the logger, this is rough, still a work in progress, but I wanted to get the version control going asap. Also added prototype dev board files
    [ADC.brd, ADC.sch, Logger_v2.sch, SAM21.brd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]
2017-03-30 PCB Complete, Ready for Checking
    PCB is functionally complete, ready for double checking and verification.
    Note: Still should switch battery clip
    [ALog_BottleLogger_bill_of_materials.xls, BatteryModule.sch, Logger_v2.brd, logger.brd]
2017-04-01 PCB Major Issues Fixed
    All major issues on the PCB are fixed and only remaining problems are with solder mask spacing. Ready for final functional check
    [Logger_v2.GBL, Logger_v2.GBO, Logger_v2.GBS, Logger_v2.GTL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]
2017-04-07 Final PCB Logger Design
    The final design iteration for the logger PCB
    [LoggerV2 BOM.xlsx, Logger_v2 (OrderingInfo).csv, Logger_v2.GBL, Logger_v2.GBO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]
2017-04-12 Added complete battery board schematic
    Added a complete and functional schematic for the battery board, revisions still pending should be functional
    [BatteryModule.sch]

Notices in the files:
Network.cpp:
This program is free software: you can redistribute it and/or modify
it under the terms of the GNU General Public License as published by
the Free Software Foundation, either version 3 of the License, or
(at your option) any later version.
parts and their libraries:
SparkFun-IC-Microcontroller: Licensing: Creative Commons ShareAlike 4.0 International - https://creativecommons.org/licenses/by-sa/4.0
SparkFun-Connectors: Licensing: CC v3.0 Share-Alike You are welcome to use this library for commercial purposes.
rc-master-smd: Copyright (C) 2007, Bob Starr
